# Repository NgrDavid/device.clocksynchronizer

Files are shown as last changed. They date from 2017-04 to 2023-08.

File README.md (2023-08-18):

## Harp Clock Synchronizer ##

Outputs clock synchronization for up to 6 Harp devices when in "Generator" mode. If there is a need to synchronize more devices, the device can be set to "Repeater" mode and receive a master clock signal from another Clock Synchronizer device set to "Generator" mode.

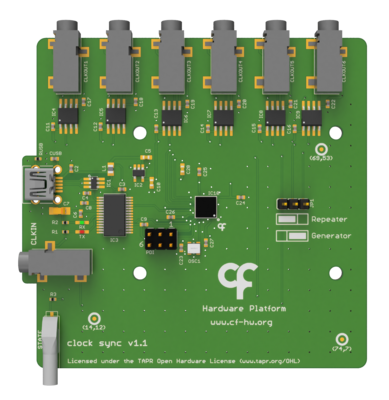
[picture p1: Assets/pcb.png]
harpclocksync


### Key Features ###

* Can be used as a Generator (up to 6 devices) or Repeater.
* Synchronization error: ± 42 µS

### Connectivity ###

* 1x clock sync input (CLKIN) [stereo jack]
* 1x USB (for power) [USB type B]
* 6x clock sync output (CLKOUT1 to CLKOUT6) [stereo jack]

## Interface ##

The interface with the Harp board can be done through [Bonsai](https://bonsai-rx.org/).

## Licensing ##

Each subdirectory will contain a license or, possibly, a set of licenses if it involves both hardware and software.

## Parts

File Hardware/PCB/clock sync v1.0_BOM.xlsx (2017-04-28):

Board | Part(s) | Quantity | Description | Distributor | Part. No.
 | IC1 | 1 | ESD Protection Low Cap | Mouser | 511-USBLC6-2SC6
 | IC2 | 1 | LDO 250mA Ultra-Lo Noise LDO Reg | Mouser | 595-LP5907MFX-3.3NPB
 | IC3 | 1 | IC USB USB to Serial UART Enhanced IC SSOP-28 | Mouser | 895-FT232RL
 | IC4, IC5, IC6, IC7, IC8, IC9 | 6 | Isoladores digitais Single Ch 3.75kV Iso 150M 1/0, def out=LO | Mouser | 634-SI8610BC-B-IS
 | IC10 | 1 | ATXMEGA64A4U-AU, ATxmega, 32 MHz, 64 KB, 4 KB, 44, TQFP | Mouser | 556-ATXMEGA64A4U-AU
 | C3, C4 | 2 | CAP CER 47pF 50V ±5% C0G 0402 | Mouser | 77-VJ0402A470JXACBC
 | CUSB | 1 | CAP CER 4.7nF 100V ±10% X7R 0402 | Mouser | 81-GRM155R72A472KA01
 | C2, C6, C8, C9, C11, C12, C13, C14, C15, C16, C17, C18, C19, C20, C21, C22, C23, C24, C25, C26 | 20 | CAP CER 100nF 10V X5R 0402 | REEL | REEL
 | C27 | 1 | CAP CER 0.33uF 10V ±10% X5R 0402 | Mouser | GRM155R61A334KE15D
 | C7 | 1 | CAP TAN 4.7uF 6.3V ±10% 1206 | Mouser | 80-T491A475K006
 | C5, C10, C28 | 3 | CAP CER 10uF 10V ±10% X5R 0603 | Mouser | 81-GRM188R61A106KE9D
 | R3 | 1 | RES SMD 68Ω OHM 5% 0402 | Mouser | 71-CRCW0402-68-E3
 | RUSB | 1 | RES SMD 1MΩ 1% 0402 | Mouser | 652-CR0402FX-1004GLF
 | L1 | 1 | 40ohms 100MHz 1.5A Monolithic 0805 SMD | Mouser | 875-MI0805K400R-10
 | STATE | 1 | LED, Green, 1.6mm x 0.8mm, 566 nm, 2.1 V, 20 mA, 15 mcd | Mouser | 78-TLMP1100-GS08
 | OSC1 | 1 | 32MHz 10ppm | Mouser | 998-1001CI5032.0000T
 | PDI | 1 | 6P DR UNSHRD HRD | Mouser | 649-67996-206HLF
 | JP1 | 1 | 3POS Gold Male | Mouser | 649-68001-203HLF
 |  | 1 | SHUNT JUMPER, 2POS | Farnell | 2396301
 | USB | 1 | UX60-MB-5S8 | Mouser | 798-UX60-MB-5S8
 | USB Cable | 1 | USB A - MINI-B 0.8M - MINI-B 0.8M BLACK | Mouser | 538-88732-8502
 | CLKIN, CLKOUT1-6 | 7 | SMT 3.5 STEREO REEL | Mouser | 502-35RASMT2BHNTRX
 |  | 1 | Tubos de Luz LED CML LIGHTPIPE | Mouser | 606-7513D2-L
 |  | 5 | 3.5mm Stereo Jack Plug, 3.5mm Stereo Jack Plug, 3.9 ft, 1.2 m, Black | Farnell | 3712278
 |  | 1 | 3.5mm Stereo Jack Plug, 3.5mm Stereo Jack Plug, 16 ft, 5 m, Black | Farnell | 3712527
 | Components | 62
 | Licensed under the TAPR Open Hardware License (www.tapr.org/OHL)
 | Copyright 2017 Artur Silva and Filipe Carvalho

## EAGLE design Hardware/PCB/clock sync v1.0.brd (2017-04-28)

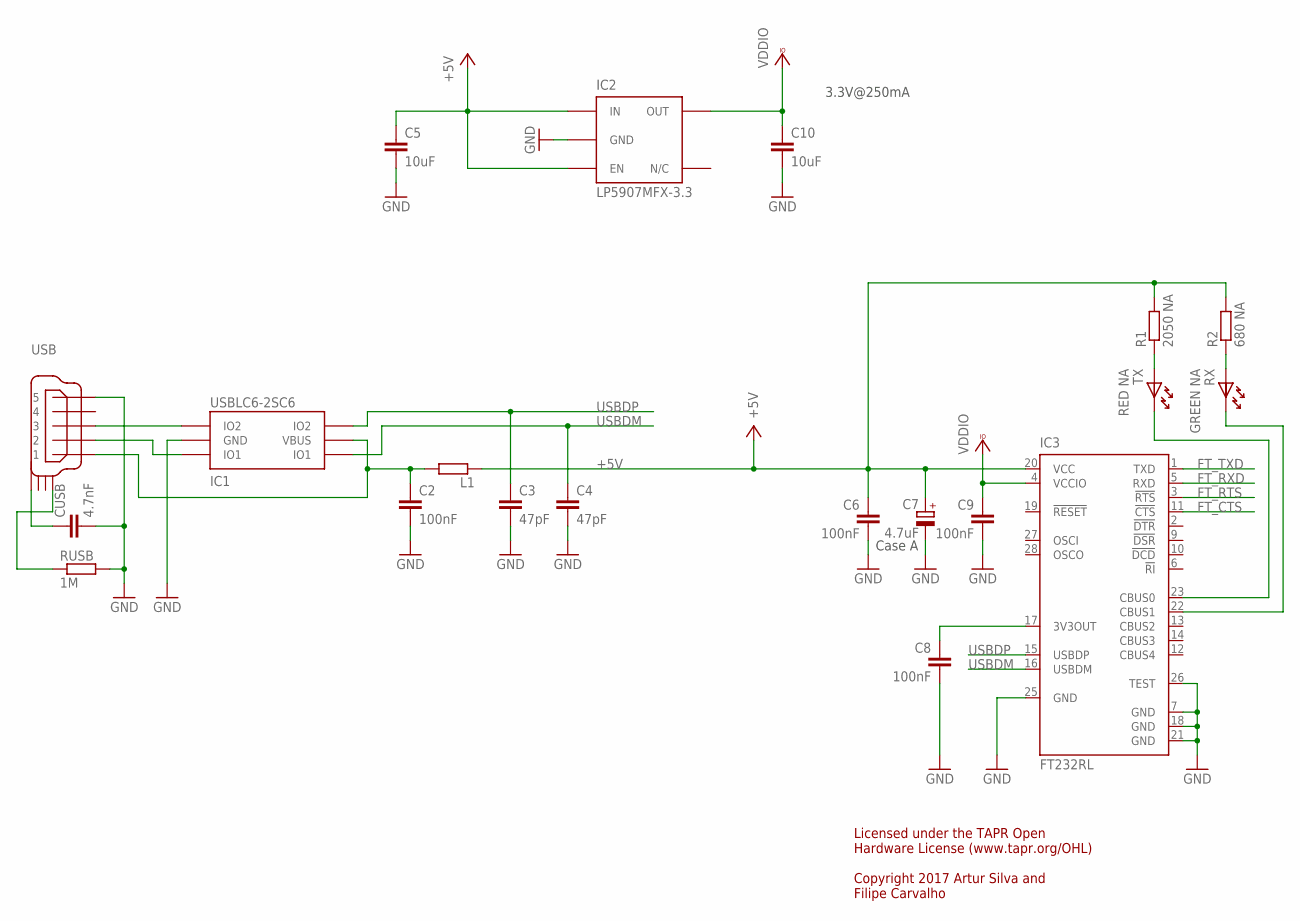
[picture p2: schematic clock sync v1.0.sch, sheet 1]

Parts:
C2, C6, C8, C9: 100nF; C0402
C3, C4: 47pF; C0402
C5, C10: 10uF; C0603
C7: 4.7uF; A/3216-18W
CUSB: 4.7nF; C0402
IC1: USBLC6-2SC6; SOT23-6L
IC2: LP5907MFX-3.3; TSOT23-5
IC3: FT232RL; SSOP28
L1: ???; R0805
R1: 2050 NA; R0402
R2: 680 NA; R0402
RUSB: 1M; R0402
RX: GREEN NA; LED_HAND
TX: RED NA; LED_HAND
USB: USB_MINI_B; 240-0002-1

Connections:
+5V: C5.1, C6.1, C7.+, IC2.1 (IN), IC2.3 (EN), IC3.20 (VCC), L1.1, R1.2, R2.2
FT_CTS: IC3.11 (!CTS); also elsewhere on the board
FT_RTS: IC3.3 (!RTS); also elsewhere on the board
FT_RXD: IC3.5 (RXD); also elsewhere on the board
FT_TXD: IC3.1 (TXD); also elsewhere on the board
GND: C2.2, C3.2, C4.2, C5.2, C6.2, C7.-, C8.2, C9.2, C10.2, CUSB.2, IC1.P$2 (GND), IC2.2 (GND), IC3.7 (GND), IC3.18 (GND), IC3.21 (GND), IC3.25 (GND), IC3.26 (TEST), RUSB.2, USB.P$5 (5); also elsewhere on the board
unnamed: C8.1, IC3.17 (3V3OUT)
unnamed: C2.1, IC1.P$5 (VBUS), L1.2, USB.P$1 (1)
unnamed: IC1.P$1 (IO1), USB.P$2 (2)
unnamed: R2.1, RX.A
unnamed: IC3.23 (CBUS0), TX.K
unnamed: IC3.22 (CBUS1), RX.K
unnamed: IC1.P$3 (IO2), USB.P$3 (3)
unnamed: CUSB.1, USB.SHIELD_4
unnamed: RUSB.1, USB.SHIELD_1
unnamed: R1.1, TX.A
USBDM: C4.1, IC1.P$6 (IO1), IC3.16 (USBDM)
USBDP: C3.1, IC1.P$4 (IO2), IC3.15 (USBDP)
VCCIO: C9.1, C10.1, IC2.5 (OUT), IC3.4 (VCCIO); also elsewhere on the board

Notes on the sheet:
Case A
3.3V@250mA
Licensed under the TAPR Open Hardware License (www.tapr.org/OHL) Copyright 2017 Artur Silva and Filipe Carvalho

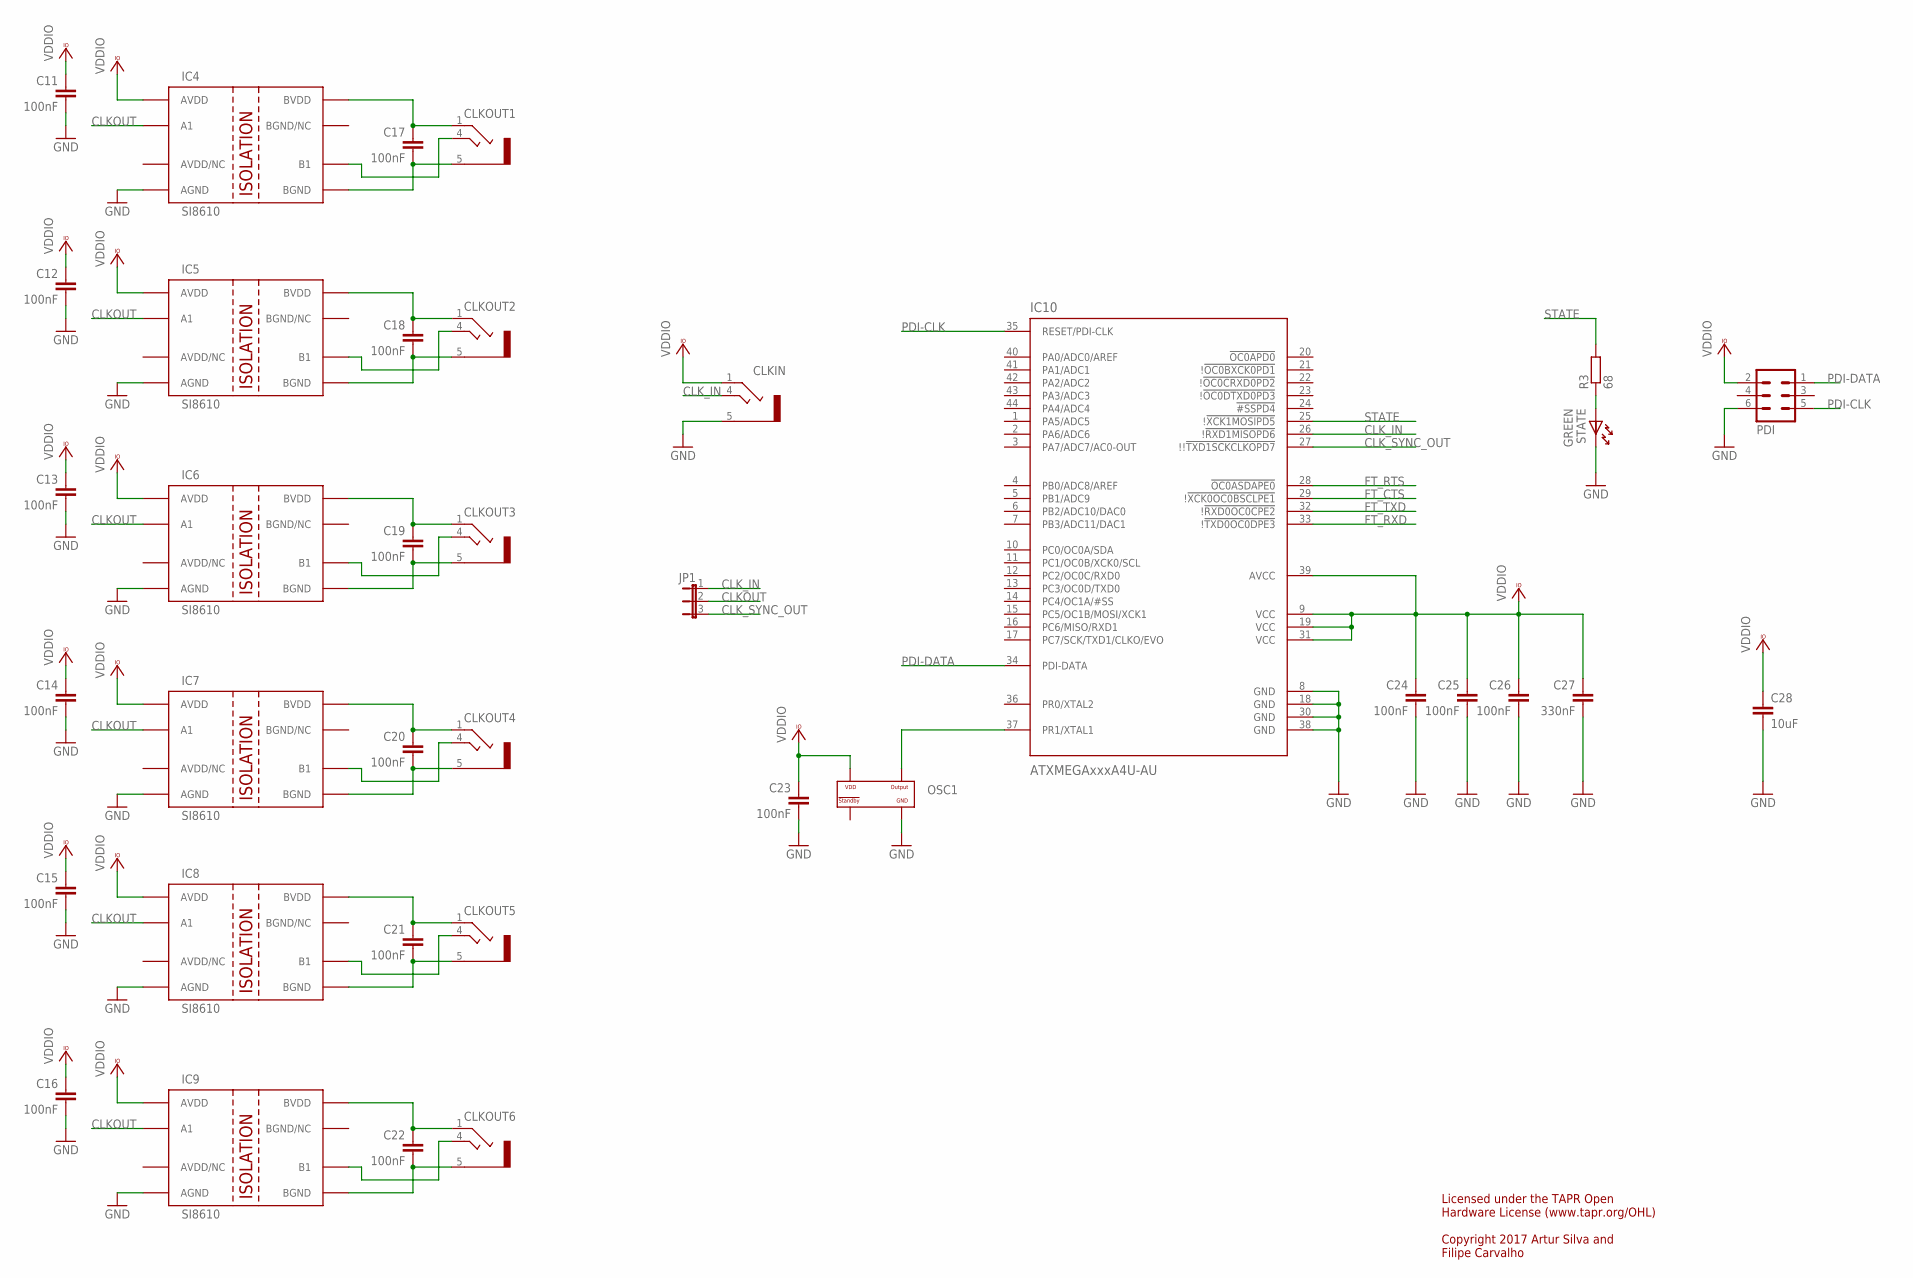
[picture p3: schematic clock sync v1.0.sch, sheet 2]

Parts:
C11, C12, C13, C14, C15, C16, C17, C18, C19, C20, C21, C22, C23, C24, C25, C26: 100nF; C0402
C27: 330nF; C0402
C28: 10uF; C0603
CLKIN: STEREO_JACK; 35RASMT2BHNTRX
CLKOUT1, CLKOUT2, CLKOUT3, CLKOUT4, CLKOUT5, CLKOUT6: STEREO_JACK; 35RASMT2BHNTRX
IC4, IC5, IC6, IC7, IC8, IC9: SI8610; SO-08
IC10: ATXMEGAxxxA4U-AU; QFP80P1200X1200X120-44N
JP1: JP2E"; JP2_NO_NUMBERS
OSC1: OSCILLATOR; OSCILLATOR_3.2X2.5
PDI: MA03-2
R3: 68; R0402
STATE: GREEN; LED_HAND

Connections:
CLKOUT: IC4.2 (A1), IC5.2 (A1), IC6.2 (A1), IC7.2 (A1), IC8.2 (A1), IC9.2 (A1), JP1.2
CLK_IN: CLKIN.4, IC10.26 (!!RXD1MISOPD6), JP1.1
CLK_SYNC_OUT: IC10.27 (!!!TXD1SCKCLKOPD7), JP1.3
FT_CTS: IC10.29 (!!XCK0OC0BSCLPE1); also elsewhere on the board
FT_RTS: IC10.28 (!OC0ASDAPE0); also elsewhere on the board
FT_RXD: IC10.33 (!!TXD0OC0DPE3); also elsewhere on the board
FT_TXD: IC10.32 (!!RXD0OC0CPE2); also elsewhere on the board
GND: C11.2, C12.2, C13.2, C14.2, C15.2, C16.2, C23.2, C24.2, C25.2, C26.2, C27.2, C28.2, CLKIN.5, IC4.4 (AGND), IC5.4 (AGND), IC6.4 (AGND), IC7.4 (AGND), IC8.4 (AGND), IC9.4 (AGND), IC10.8 (GND), IC10.18 (GND), IC10.30 (GND), IC10.38 (GND), OSC1.P$2 (GND), PDI.6, STATE.K; also elsewhere on the board
unnamed: CLKOUT1.4, IC4.6 (B1)
unnamed: C18.1, CLKOUT2.1, IC5.8 (BVDD)
unnamed: C18.2, CLKOUT2.5, IC5.5 (BGND)
unnamed: CLKOUT2.4, IC5.6 (B1)
unnamed: C19.1, CLKOUT3.1, IC6.8 (BVDD)
unnamed: C19.2, CLKOUT3.5, IC6.5 (BGND)
unnamed: CLKOUT3.4, IC6.6 (B1)
unnamed: C20.1, CLKOUT4.1, IC7.8 (BVDD)
unnamed: C20.2, CLKOUT4.5, IC7.5 (BGND)
unnamed: CLKOUT4.4, IC7.6 (B1)
unnamed: C21.1, CLKOUT5.1, IC8.8 (BVDD)
unnamed: C21.2, CLKOUT5.5, IC8.5 (BGND)
unnamed: C17.1, CLKOUT1.1, IC4.8 (BVDD)
unnamed: CLKOUT5.4, IC8.6 (B1)
unnamed: C22.1, CLKOUT6.1, IC9.8 (BVDD)
unnamed: C22.2, CLKOUT6.5, IC9.5 (BGND)
unnamed: C17.2, CLKOUT1.5, IC4.5 (BGND)
unnamed: CLKOUT6.4, IC9.6 (B1)
unnamed: R3.1, STATE.A
OSC1: IC10.37 (PR1/XTAL1), OSC1.P$3 (OUTPUT)
PDI-CLK: IC10.35 (RESET/PDI-CLK), PDI.5
PDI-DATA: IC10.34 (PDI-DATA), PDI.1
STATE: IC10.25 (!!XCK1MOSIPD5), R3.2
VCCIO: C11.1, C12.1, C13.1, C14.1, C15.1, C16.1, C23.1, C24.1, C25.1, C26.1, C27.1, C28.1, CLKIN.1, IC4.1 (AVDD), IC5.1 (AVDD), IC6.1 (AVDD), IC7.1 (AVDD), IC8.1 (AVDD), IC9.1 (AVDD), IC10.9 (VCC), IC10.19 (VCC), IC10.31 (VCC), IC10.39 (AVCC), OSC1.P$4 (VDD), PDI.2; also elsewhere on the board

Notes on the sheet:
Licensed under the TAPR Open Hardware License (www.tapr.org/OHL) Copyright 2017 Artur Silva and Filipe Carvalho

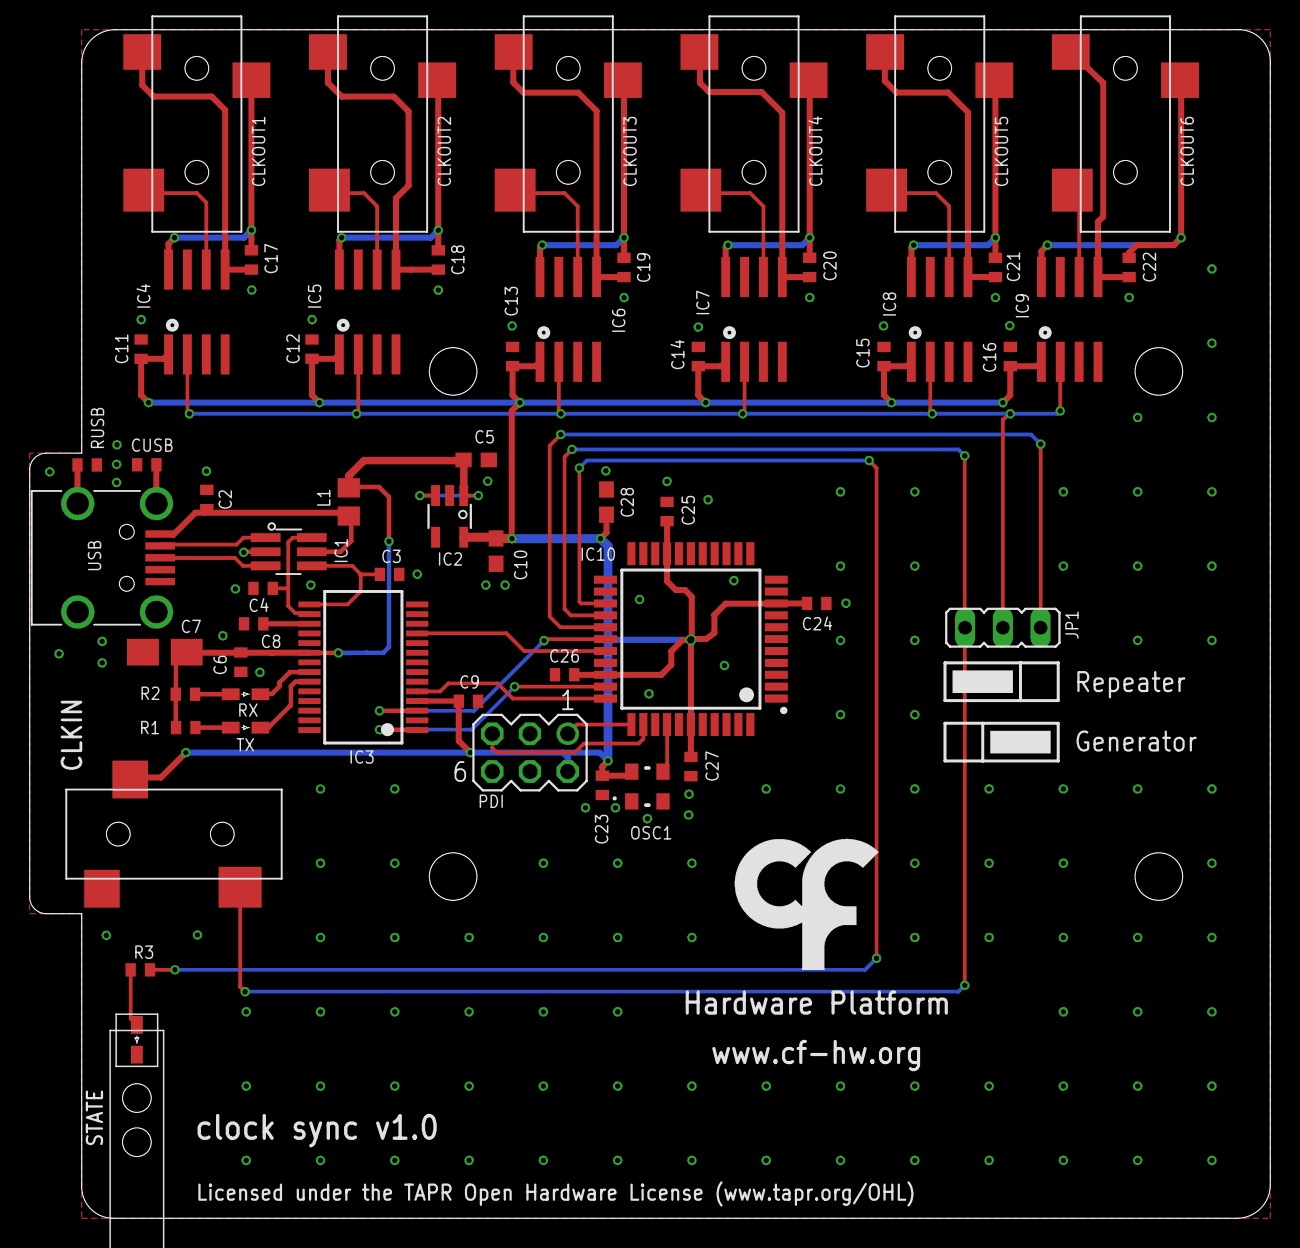
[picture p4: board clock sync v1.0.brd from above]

Board: 2 copper layers, 83.5 x 80.0 mm, 59 parts (0 on the bottom side), 45 nets.

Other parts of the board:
U$1: LED_PIPE_7513D2-L
U$9: LOGO_6

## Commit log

2017-04-21 Added entire files set.
    [registers.xls]
2017-04-28 Added the PCB files.
    [clock sync BOM.xlsx, clock sync.brd, clock sync.sch]
2018-01-11 Updated to Atxmega Harp core version 1.1.
    [registers.xls]
2022-12-17 Rename files
    [clock sync v1.0.brd, clock sync v1.0.sch, clock sync v1.0_BOM.xlsx]
2022-12-17 Renamed files
    [clock sync BOM.xlsx, clock sync.brd, clock sync.sch]
2022-12-23 refactor repository structure
    [clock sync v1.0.brd, clock sync v1.0.sch, clock sync v1.0_BOM.xlsx]
2023-08-18 Add device schema
2023-08-18 Add generated device interface
2023-08-20 Update PCB image asset
2024-11-13 Update device schema source
